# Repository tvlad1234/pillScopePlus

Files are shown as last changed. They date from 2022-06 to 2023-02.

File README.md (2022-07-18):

# pillScope Plus
Oscilloscope based around the STM32F401 Black Pill and a color LCD screen, meant to be used as an educational tool
The pillScope in its case

## Why does it exist?
The goal of this project was to create a simple and easy to build but still very usable oscillsocope. I wanted to learn the basics of how a **digital storage oscilloscope** functions, while also ending up with something which can be used as an educational tool in the lab. A short description of how oscillscopes (and this one in particular) work can be found [here](HowItWorks.md).

## Features
* -3.3V to 3.3V input range (can be increased if using attenuator probes)
* 1MOhm input impedance
* 10uS/div minimum timebase
* 1.6 MSa/S sampling rate
* On screen measurements:
  * min/max voltage
  * peak-to-peak voltage
  * frequency
* Captured waveforms can be sent to a computer over UART and analyzed in the Tektronix TekScope app
## Required parts
### Base parts:
* STM32F401CC Black Pill development board
* 128x160 ST7735-based TFT display
* 3 pushbuttons
* LM358 dual op-amp (rail-to-rail opamps should work better in this context, but this is what I had on hand)
* 2x 68kOhm resistors (to create a 1.65V offset voltage)
* 2x 500kOhm resistors (to create the input attenuator)

### Useful, but not mandatory:
* a 5V power supply
* an opto-isolated USB UART adapter
* a BNC connector, for using proper oscilloscope probes

## Schematics
The LCD screen is connected to SPI1 (PB3-SCK, PB5-MOSI, PB12-CS, PB13-RST, PB14-DC). The buttons are connected as follows:
* PB9: Up
* PB8: Select
* PB7: Down

The output of the analog frontend is connected to ADC1_IN0, which corresponds to PA0.\
The schematic of the frontend can be found in the [frontend.pdf](frontend.pdf) file.

## Using the oscilloscope
### The UI
The Select button cycles through the different parameters, which can be adjusted using the Up and Down buttons. 

### Auto calibration
Pressing Up and Down at the same time triggers the auto-calibration function. The tip and ground clip of the probed should be coupled together while calibrating. 

### Measuring things
The frontend of the instrument makes use of a virtual ground point which is 1.65V above the real ground. Because of this, the oscilloscope and the device under test must not be sharing the same ground reference. If you need to send data to the computer while measuring a device which shares ground with the scope, you should connect the computer via an opto-isolated adapter, while powering the oscilloscope from an external source.

### Saving captured wavevorms
The captured waveforms can be sent to a computer over UART.

#### CSV Output
Sending `s` (lowercase s) to the UART tells the instrument to output the captured waveform in CSV format, which is compatible with the Tektronix TekScope app.

putty

#### Direct TekScope output 
Sending `S` (capital S) tells the scope to output raw data, which can be read by a [companion app](https://github.com/tvlad1234/tekscopeIngest). This app automatically streams the captured data to TekScope, which allows almost real-time waveform analysis on the computer.
companion

## Code
The code can be compiled with `make`. The actual oscilloscope code of this project is located in `Core\Src`, the [scope.c](Core/Src/scope.c), [ui.c](Core/Src/ui.c) and [wave.c](Core/Src/wave.c) files. Feel free to take a look, as they're commented for ease of understanding.

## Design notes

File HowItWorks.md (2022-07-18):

# How does it work?
## But first of all, what's an oscilloscope?
An oscilloscope, colloquially called _scope_ is a measurement instrument which graphically displays electrical voltage in relation to time. This allows the user to visualise and analyze high-speed electrical signals which cannot be seen otherwise.

In the past, oscilloscopes were constructed using cathode ray tubes, similar to the ones found in old TVs. They worked by sweeping an electron beam across a phosphor-coated screen, which was being vertically deflected by the input signal. This would cause the screen to glow in every point struck by the beam, allowing visualisation of the input signal as a waveform. This process was purely analog and happened in real-time. As such, all measurements had to be done manually, by physically measuring the waveform on the screen. This also meant that the waveforms couldn't be stored anywhere (analog storage oscilloscopes existed but they were very uncommon). 

Most oscilloscopes nowadays are *digital storage oscillscopes*. As their name suggests, they sample and store the incoming signal in a digital manner. This way, the signal can be analyzed using a computer, making advanced and automatic measurements possible.

## How does a digital storage oscilloscope work?
### Conditioning the signal
Before it can be measured by the various components of an oscilloscope, the input signal must be conditioned in some way. This usually involves scaling and attenuating it by a component called the *analog frontend*. The actual measuring element of our instrument can only sample voltages in the 0 - 3.3V range. In order to extend this range into a useful domain, we attenuate the input signal by half and center it at around 1.65V. This is done by using a voltage divider and an op-amp to create a reference voltage and another divider and opamp to attenuate and buffer the signal. Doing so allows the instrument measure voltages ranging from -3.3V to +3.3V. The schematic of the frontend can be found in the [frontend.pdf](frontend.pdf) file.

### Converting voltage into numbers
Electrical voltage is a physical quantity which must be sampled and quantized into a numerical value. This is done by an _ADC_ (**A**nalog to **D**igital **C**onverter). The ADC used in this project is integrated into the microcontroller and it's a *successive aproximation register ADC*. This means that the ADC takes the input voltage and compares it to different voltages until it finds the closest match. Two of the main characteristics of an ADC are its resolution and maximum sampling rate. The resolution tells us how many bits it uses to represent numbers. Our ADC is 12-bit, meaning that there are 2<sup>12</sup> different values it can output. The maximum sampling rate measures how fast the ADC can measure the incoming signal. Our ADC is capable of up to 1.6 MSa/S (megasamples per second, or milions of samples per second).

### Sampling a signal
In order to digitally reconstruct a waveform, the signal must be sampled at precise intervals of time. We're achieving this by using one of the timers of our microcontroller in order to generate the timebase of our scope. This way, the ADC captures a sample on every firing of the timer. Oscilloscopes generally use dedicated hardware to trigger the sampling on precise segments of the input signal. For the sake of simplicity, our oscilloscope simulates this in software by aligning the displayed waveform with the selected trigger condition.

### Getting the data into the memory
Digital oscilloscopes usually have dedicated sample memory and hardware which handles the transfer of data from the ADC without the main processor being involved. We're using a similar approach here too, by making use of the *DMA* (**D**irect **M**emory **A**ccess) engine of the microcontroller. The processor tells the DMA to start pulling data from the ADC into a buffer in memory and then waits. Each time the ADC is triggered, a DMA transfer occurs. Once the buffer is full, the DMA stops and tells the processor that it has finished transfering data. With the sampled signal in memory, we can now display the waveform on the screen and perform different measurements.

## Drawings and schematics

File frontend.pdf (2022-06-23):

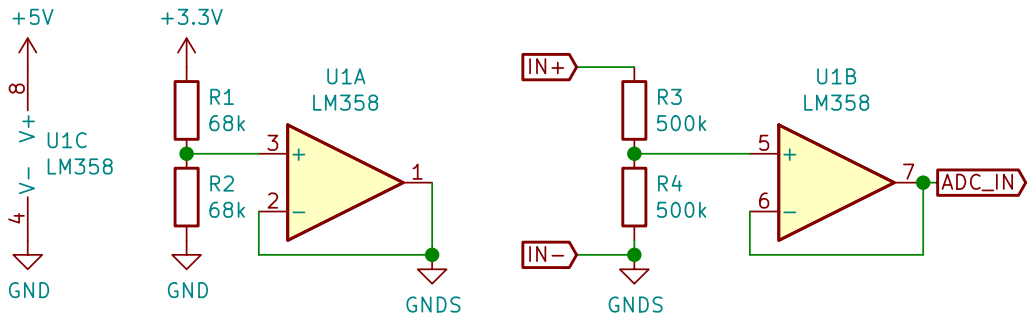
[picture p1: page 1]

File: pillScope.sch Sheet: / tvlad1234 V- 4 V+

Id: 1/1 Title: pillScope analog frontend

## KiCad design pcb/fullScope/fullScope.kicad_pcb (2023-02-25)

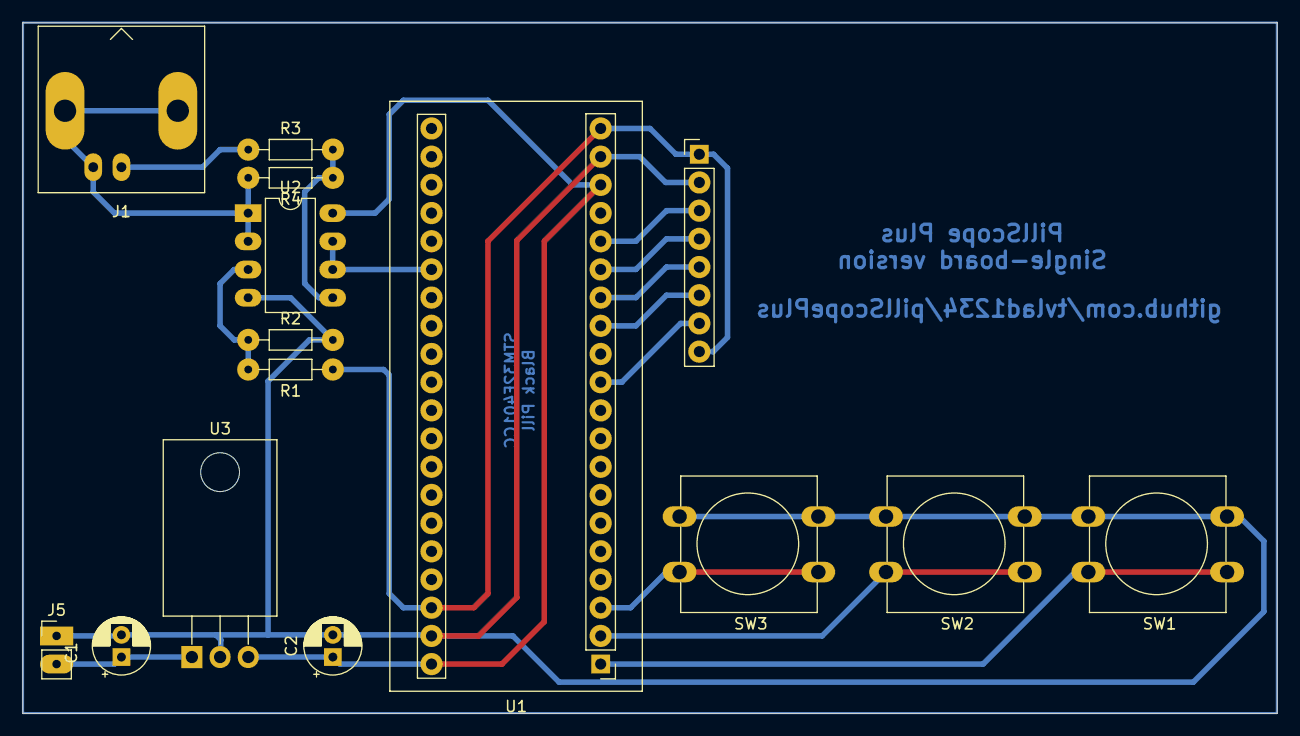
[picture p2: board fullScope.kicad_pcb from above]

Board: 2 copper layers, 113.0 x 62.2 mm, 15 parts (0 on the bottom side), 17 nets.

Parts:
C1: 10 uF; CP_Radial_D5.0mm_P2.00mm
C2: 100 uF; CP_Radial_D5.0mm_P2.00mm
J1: IN; BNC_Amphenol_B6252HB-NPP3G-50_Horizontal
J3: LCD; PinHeader_1x08_P2.54mm_Vertical
J5: Vin; PinHeader_1x02_P2.54mm_Vertical
R1, R2: R; R_Axial_DIN0204_L3.6mm_D1.6mm_P7.62mm_Horizontal
R3, R4: 500k; R_Axial_DIN0204_L3.6mm_D1.6mm_P7.62mm_Horizontal
SW1: Btn 1; SW_PUSH-12mm
SW2: Btn 2; SW_PUSH-12mm
SW3: Btn 3; SW_PUSH-12mm
U1: F401CC; YAAJ_WeAct_BlackPill_2
U2: LM358; DIP-8_W7.62mm_LongPads
U3: LM7805; TO-220-3_Horizontal_TabDown

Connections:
+3.3V: J3.1, J3.8, R1.1, U1.20 (3V3), U1.38 (3V3)
+5V: C2.1, U1.18 (5V), U1.40 (5V), U2.8 (V+), U3.3 (VO)
+9V: C1.1, J5.2, U3.1 (VI)
BTN1: SW1.1, U1.1 (PB12)
BTN2: SW2.1, U1.2 (PB13)
BTN3: SW3.1, U1.3 (PB14)
CS: J3.3, U1.16 (PB8)
DC: J3.5, U1.14 (PB6)
FE_OUT: U1.26 (PA0), U2.6 (-), U2.7
GND: C1.2, C2.2, J3.2, J5.1, R2.2, SW1.2, SW2.2, SW3.2, U1.19 (GND), U1.39 (GND), U2.4 (V-), U3.2 (GND)
GNDS: J1.2 (Ext), R4.2, U2.1, U2.2 (-)
IN+: J1.1 (In), R3.1
MOSI: J3.6, U1.13 (PB5)
unnamed: R1.2, R2.1, U2.3 (+)
unnamed: R3.2, R4.1, U2.5 (+)
RES: J3.4, U1.15 (PB7)
SCK: J3.7, U1.11 (PB3)

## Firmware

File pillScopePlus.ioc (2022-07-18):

#MicroXplorer Configuration settings - do not modify
ADC1.ExternalTrigConv=ADC_EXTERNALTRIGCONV_T3_TRGO
ADC1.IPParameters=master,NbrOfConversionFlag,ExternalTrigConv
ADC1.NbrOfConversionFlag=1
ADC1.master=1
Dma.ADC1.0.Direction=DMA_PERIPH_TO_MEMORY
Dma.ADC1.0.FIFOMode=DMA_FIFOMODE_ENABLE
Dma.ADC1.0.FIFOThreshold=DMA_FIFO_THRESHOLD_FULL
Dma.ADC1.0.Instance=DMA2_Stream0
Dma.ADC1.0.MemBurst=DMA_MBURST_SINGLE
Dma.ADC1.0.MemDataAlignment=DMA_MDATAALIGN_HALFWORD
Dma.ADC1.0.MemInc=DMA_MINC_ENABLE
Dma.ADC1.0.Mode=DMA_NORMAL
Dma.ADC1.0.PeriphBurst=DMA_PBURST_SINGLE
Dma.ADC1.0.PeriphDataAlignment=DMA_PDATAALIGN_HALFWORD
Dma.ADC1.0.PeriphInc=DMA_PINC_DISABLE
Dma.ADC1.0.Priority=DMA_PRIORITY_HIGH
Dma.ADC1.0.RequestParameters=Instance,Direction,PeriphInc,MemInc,PeriphDataAlignment,MemDataAlignment,Mode,Priority,FIFOMode,FIFOThreshold,MemBurst,PeriphBurst
Dma.MEMTOMEM.1.Direction=DMA_MEMORY_TO_MEMORY
Dma.MEMTOMEM.1.FIFOMode=DMA_FIFOMODE_ENABLE
Dma.MEMTOMEM.1.FIFOThreshold=DMA_FIFO_THRESHOLD_FULL
Dma.MEMTOMEM.1.Instance=DMA2_Stream1
Dma.MEMTOMEM.1.MemBurst=DMA_MBURST_SINGLE
Dma.MEMTOMEM.1.MemDataAlignment=DMA_MDATAALIGN_BYTE
Dma.MEMTOMEM.1.MemInc=DMA_MINC_ENABLE
Dma.MEMTOMEM.1.Mode=DMA_NORMAL
Dma.MEMTOMEM.1.PeriphBurst=DMA_PBURST_SINGLE
Dma.MEMTOMEM.1.PeriphDataAlignment=DMA_PDATAALIGN_BYTE
Dma.MEMTOMEM.1.PeriphInc=DMA_PINC_ENABLE
Dma.MEMTOMEM.1.Priority=DMA_PRIORITY_LOW
Dma.MEMTOMEM.1.RequestParameters=Instance,Direction,PeriphInc,MemInc,PeriphDataAlignment,MemDataAlignment,Mode,Priority,FIFOMode,FIFOThreshold,MemBurst,PeriphBurst
Dma.Request0=ADC1
Dma.Request1=MEMTOMEM
Dma.RequestsNb=2
File.Version=6
GPIO.groupedBy=Group By Peripherals
KeepUserPlacement=false
Mcu.CPN=STM32F401CCU6
Mcu.Family=STM32F4
Mcu.IP0=ADC1
Mcu.IP1=DMA
Mcu.IP2=NVIC
Mcu.IP3=RCC
Mcu.IP4=SPI1
Mcu.IP5=SYS
Mcu.IP6=TIM3
Mcu.IP7=USART1
Mcu.IPNb=8
Mcu.Name=STM32F401C(B-C)Ux
Mcu.Package=UFQFPN48
Mcu.Pin0=PC13-ANTI_TAMP
Mcu.Pin1=PH0 - OSC_IN
Mcu.Pin10=PA14
Mcu.Pin11=PB3
Mcu.Pin12=PB5
Mcu.Pin13=PB7
Mcu.Pin14=PB8
Mcu.Pin15=PB9
Mcu.Pin16=VP_SYS_VS_Systick
Mcu.Pin17=VP_TIM3_VS_ClockSourceINT
Mcu.Pin2=PH1 - OSC_OUT
Mcu.Pin3=PA0-WKUP
Mcu.Pin4=PB12
Mcu.Pin5=PB13
Mcu.Pin6=PB14
Mcu.Pin7=PA9
Mcu.Pin8=PA10
Mcu.Pin9=PA13
Mcu.PinsNb=18
Mcu.ThirdPartyNb=0
Mcu.UserConstants=
Mcu.UserName=STM32F401CCUx
MxCube.Version=6.5.0
MxDb.Version=DB.6.0.50
NVIC.BusFault_IRQn=true\:0\:0\:false\:false\:true\:false\:false\:true
NVIC.DMA2_Stream0_IRQn=true\:0\:0\:false\:false\:true\:false\:true\:true
NVIC.DMA2_Stream1_IRQn=true\:0\:0\:false\:false\:true\:true\:true\:true
NVIC.DebugMonitor_IRQn=true\:0\:0\:false\:false\:true\:false\:false\:true
NVIC.ForceEnableDMAVector=true
NVIC.HardFault_IRQn=true\:0\:0\:false\:false\:true\:false\:false\:true
NVIC.MemoryManagement_IRQn=true\:0\:0\:false\:false\:true\:false\:false\:true
NVIC.NonMaskableInt_IRQn=true\:0\:0\:false\:false\:true\:false\:false\:true
NVIC.PendSV_IRQn=true\:0\:0\:false\:false\:true\:false\:false\:true
NVIC.PriorityGroup=NVIC_PRIORITYGROUP_4
NVIC.SVCall_IRQn=true\:0\:0\:false\:false\:true\:false\:false\:true
NVIC.SysTick_IRQn=true\:15\:0\:false\:false\:true\:false\:true\:true
NVIC.USART1_IRQn=true\:0\:0\:false\:false\:true\:true\:true\:true
NVIC.UsageFault_IRQn=true\:0\:0\:false\:false\:true\:false\:false\:true
PA0-WKUP.Signal=ADCx_IN0
PA10.Mode=Asynchronous
PA10.Signal=USART1_RX
PA13.Mode=Serial_Wire
PA13.Signal=SYS_JTMS-SWDIO
PA14.Mode=Serial_Wire
PA14.Signal=SYS_JTCK-SWCLK
PA9.Mode=Asynchronous
PA9.Signal=USART1_TX
PB12.GPIOParameters=GPIO_Label
PB12.GPIO_Label=ST7735_CS
PB12.Locked=true
PB12.Signal=GPIO_Output
PB13.GPIOParameters=GPIO_Label
PB13.GPIO_Label=ST7735_RES
PB13.Locked=true
PB13.Signal=GPIO_Output
PB14.GPIOParameters=GPIO_Label
PB14.GPIO_Label=ST7735_DC
PB14.Locked=true
PB14.Signal=GPIO_Output
PB3.Locked=true
PB3.Mode=TX_Only_Simplex_Unidirect_Master
PB3.Signal=SPI1_SCK
PB5.Locked=true
PB5.Mode=TX_Only_Simplex_Unidirect_Master
PB5.Signal=SPI1_MOSI
PB7.GPIOParameters=GPIO_PuPd,GPIO_Label
PB7.GPIO_Label=BTN1
PB7.GPIO_PuPd=GPIO_PULLUP
PB7.Locked=true
PB7.Signal=GPIO_Input
PB8.GPIOParameters=GPIO_PuPd,GPIO_Label
PB8.GPIO_Label=BTN2
PB8.GPIO_PuPd=GPIO_PULLUP
PB8.Locked=true
PB8.Signal=GPIO_Input
PB9.GPIOParameters=GPIO_PuPd,GPIO_Label
PB9.GPIO_Label=BTN3
PB9.GPIO_PuPd=GPIO_PULLUP
PB9.Locked=true
PB9.Signal=GPIO_Input
PC13-ANTI_TAMP.GPIOParameters=GPIO_Label
PC13-ANTI_TAMP.GPIO_Label=LED
PC13-ANTI_TAMP.Locked=true
PC13-ANTI_TAMP.Signal=GPIO_Output
PH0\ -\ OSC_IN.Mode=HSE-External-Oscillator
PH0\ -\ OSC_IN.Signal=RCC_OSC_IN
PH1\ -\ OSC_OUT.Mode=HSE-External-Oscillator
PH1\ -\ OSC_OUT.Signal=RCC_OSC_OUT
PinOutPanel.RotationAngle=0
ProjectManager.AskForMigrate=true
ProjectManager.BackupPrevious=false
ProjectManager.CompilerOptimize=6
ProjectManager.ComputerToolchain=false
ProjectManager.CoupleFile=false
ProjectManager.CustomerFirmwarePackage=
ProjectManager.DefaultFWLocation=true
ProjectManager.DeletePrevious=true
ProjectManager.DeviceId=STM32F401CCUx
ProjectManager.FirmwarePackage=STM32Cube FW_F4 V1.27.0
ProjectManager.FreePins=false
ProjectManager.HalAssertFull=false
ProjectManager.HeapSize=0x200
ProjectManager.KeepUserCode=true
ProjectManager.LastFirmware=false
ProjectManager.LibraryCopy=0
ProjectManager.MainLocation=Core/Src
ProjectManager.NoMain=false
ProjectManager.PreviousToolchain=
ProjectManager.ProjectBuild=false
ProjectManager.ProjectFileName=pillScopePlus.ioc
ProjectManager.ProjectName=pillScopePlus
ProjectManager.RegisterCallBack=
ProjectManager.StackSize=0x400
ProjectManager.TargetToolchain=Makefile
ProjectManager.ToolChainLocation=
ProjectManager.UnderRoot=false
ProjectManager.functionlistsort=1-SystemClock_Config-RCC-false-HAL-false,2-MX_GPIO_Init-GPIO-false-HAL-true,3-MX_DMA_Init-DMA-false-HAL-true,4-MX_ADC1_Init-ADC1-false-HAL-true,5-MX_SPI1_Init-SPI1-false-HAL-true,6-MX_TIM3_Init-TIM3-false-HAL-true,7-MX_USB_DEVICE_Init-USB_DEVICE-false-HAL-false,7-MX_USART1_UART_Init-USART1-false-HAL-true
RCC.48MHZClocksFreq_Value=50000000
RCC.AHBFreq_Value=100000000
RCC.APB1CLKDivider=RCC_HCLK_DIV2
RCC.APB1Freq_Value=50000000
RCC.APB1TimFreq_Value=100000000
RCC.APB2Freq_Value=100000000
RCC.APB2TimFreq_Value=100000000
RCC.CortexFreq_Value=100000000
RCC.FCLKCortexFreq_Value=100000000
RCC.HCLKFreq_Value=100000000
RCC.HSE_VALUE=25000000
RCC.HSI_VALUE=16000000
RCC.I2SClocksFreq_Value=96000000
RCC.IPParameters=48MHZClocksFreq_Value,AHBFreq_Value,APB1CLKDivider,APB1Freq_Value,APB1TimFreq_Value,APB2Freq_Value,APB2TimFreq_Value,CortexFreq_Value,FCLKCortexFreq_Value,HCLKFreq_Value,HSE_VALUE,HSI_VALUE,I2SClocksFreq_Value,LSE_VALUE,LSI_VALUE,PLLCLKFreq_Value,PLLM,PLLN,PLLQCLKFreq_Value,PLLSourceVirtual,RTCFreq_Value,RTCHSEDivFreq_Value,SYSCLKFreq_VALUE,SYSCLKSource,VCOI2SOutputFreq_Value,VCOInputFreq_Value,VCOOutputFreq_Value,VcooutputI2S
RCC.LSE_VALUE=32768
RCC.LSI_VALUE=32000
RCC.PLLCLKFreq_Value=100000000
RCC.PLLM=25
RCC.PLLN=200
RCC.PLLQCLKFreq_Value=50000000
RCC.PLLSourceVirtual=RCC_PLLSOURCE_HSE
RCC.RTCFreq_Value=32000
RCC.RTCHSEDivFreq_Value=12500000
RCC.SYSCLKFreq_VALUE=100000000
RCC.SYSCLKSource=RCC_SYSCLKSOURCE_PLLCLK
RCC.VCOI2SOutputFreq_Value=192000000
RCC.VCOInputFreq_Value=1000000
RCC.VCOOutputFreq_Value=200000000
RCC.VcooutputI2S=96000000
SH.ADCx_IN0.0=ADC1_IN0,IN0
SH.ADCx_IN0.ConfNb=1
SPI1.BaudRatePrescaler=SPI_BAUDRATEPRESCALER_4
SPI1.CalculateBaudRate=25.0 MBits/s
SPI1.Direction=SPI_DIRECTION_2LINES
SPI1.IPParameters=VirtualType,Mode,Direction,CalculateBaudRate,BaudRatePrescaler
SPI1.Mode=SPI_MODE_MASTER
SPI1.VirtualType=VM_MASTER
TIM3.IPParameters=TIM_MasterOutputTrigger
TIM3.TIM_MasterOutputTrigger=TIM_TRGO_UPDATE
USART1.BaudRate=9600
USART1.IPParameters=VirtualMode,BaudRate
USART1.VirtualMode=VM_ASYNC
VP_SYS_VS_Systick.Mode=SysTick
VP_SYS_VS_Systick.Signal=SYS_VS_Systick
VP_TIM3_VS_ClockSourceINT.Mode=Internal
VP_TIM3_VS_ClockSourceINT.Signal=TIM3_VS_ClockSourceINT
board=custom

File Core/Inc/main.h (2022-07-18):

/* USER CODE BEGIN Header */
/**
 ******************************************************************************
 * @file           : main.h
 * @brief          : Header for main.c file.
 *                   This file contains the common defines of the application.
 ******************************************************************************
 * @attention
 *
 * Copyright (c) 2022 STMicroelectronics.
 * All rights reserved.
 *
 * This software is licensed under terms that can be found in the LICENSE file
 * in the root directory of this software component.
 * If no LICENSE file comes with this software, it is provided AS-IS.
 *
 ******************************************************************************
 */
/* USER CODE END Header */

/* Define to prevent recursive inclusion -------------------------------------*/
#ifndef __MAIN_H
#define __MAIN_H

#ifdef __cplusplus
extern "C" {
#endif

/* Includes ------------------------------------------------------------------*/
#include "stm32f4xx_hal.h"

/* Private includes ----------------------------------------------------------*/
/* USER CODE BEGIN Includes */
#include "st7735.h"
#include "gfx.h"
/* USER CODE END Includes */

/* Exported types ------------------------------------------------------------*/
/* USER CODE BEGIN ET */

/* USER CODE END ET */

/* Exported constants --------------------------------------------------------*/
/* USER CODE BEGIN EC */

/* USER CODE END EC */

/* Exported macro ------------------------------------------------------------*/
/* USER CODE BEGIN EM */

/* USER CODE END EM */

/* Exported functions prototypes ---------------------------------------------*/
void Error_Handler(void);

/* USER CODE BEGIN EFP */
  void printFloat(float v, int decimalDigits, char s[]);
  void *dma_memcpy(void *destination, const void *source, size_t num);
/* USER CODE END EFP */

/* Private defines -----------------------------------------------------------*/
#define LED_Pin GPIO_PIN_13
#define LED_GPIO_Port GPIOC
#define ST7735_CS_Pin GPIO_PIN_12
#define ST7735_CS_GPIO_Port GPIOB
#define ST7735_RES_Pin GPIO_PIN_13
#define ST7735_RES_GPIO_Port GPIOB
#define ST7735_DC_Pin GPIO_PIN_14
#define ST7735_DC_GPIO_Port GPIOB
#define BTN1_Pin GPIO_PIN_7
#define BTN1_GPIO_Port GPIOB
#define BTN2_Pin GPIO_PIN_8
#define BTN2_GPIO_Port GPIOB
#define BTN3_Pin GPIO_PIN_9
#define BTN3_GPIO_Port GPIOB
/* USER CODE BEGIN Private defines */

/* USER CODE END Private defines */

#ifdef __cplusplus
}
#endif

#endif /* __MAIN_H */

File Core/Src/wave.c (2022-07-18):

#include "main.h"
#include "scope.h"
#include "wave.h"

#define WHITE ST7735_WHITE
#define BLACK ST7735_BLACK
#define WAVE_COLOR ST7735_YELLOW

// All kinds of variables, you'll see what these do in scope.c
extern uint16_t adcBuf[BUFFER_LEN];
extern int atten;
extern float vdiv;
extern float trigVoltage;
extern uint8_t trig, trigged;
extern int trigPoint;

extern float tdiv;
extern uint32_t sampRate;
extern float sampPer;

extern float maxVoltage, minVoltage;
extern float measuredFreq, sigPer;

extern float offsetVoltage;

uint8_t topClip, bottomClip; // Whether or not we're clipping through the graticule

// Convert ADC sample to voltage at frontend input
float frontendVoltage(uint16_t samp)
{
    return 2 * (((3.3 * samp) / 4096.0) - offsetVoltage);
}

// Convert ADC sample to voltage at ADC input
float adcToVoltage(uint16_t samp)
{
    return (3.3 * samp) / 4096.0;
}

// This function draws the graticule onto the screen
void drawGraticule(uint16_t divx, uint16_t divy, uint16_t pix)
{
    uint16_t wit = divx * pix;
    uint16_t hei = divy * pix;

    for (int i = 0; i <= wit; i += pix)
        dottedVLine(i, 0, hei);

    for (int i = 0; i <= hei; i += pix)
        dottedHLine(0, i, wit);
}

// This function draws a dotted horizontal line, used for drawing the graticule
void dottedHLine(int x, int y, int l)
{
    for (int i = 0; i <= l; i++)
    {
        if (i % 2)
            drawPixel(x + i, y, WHITE);
        else
            drawPixel(x + i, y, BLACK);
    }
}

// This function draws a dotted vertical line, used for drawing the graticule
void dottedVLine(int x, int y, int l)
{
    for (int i = 0; i <= l; i++)
    {
        if (i % 2)
            drawPixel(x, y + i, WHITE);
        else
            drawPixel(x, y + i, BLACK);
    }
}

// Draw the waveform trace on the screen
void drawTrace(uint16_t buf[], uint16_t trigPoint, uint16_t col)
{

    maxVoltage = LOWER_VOLTAGE;
    minVoltage = UPPER_VOLTAGE;

    for (int i = 0; i <= BUFFER_LEN / 2; i++)
    {
        // If we're looping through the buffer, let's compute the minimum and maximum voltage values while we're at it
        float voltage1 = atten * frontendVoltage(buf[i + trigPoint]);
        float voltage2 = atten * frontendVoltage(buf[i + trigPoint + 1]);
        if (voltage2 > maxVoltage)
            maxVoltage = voltage2;
        if (voltage2 < minVoltage)
            minVoltage = voltage2;

        // Draw lines between sample points
        topClip = 0;
        bottomClip = 0;
        int16_t y1 = (PIXDIV * YDIV / 2 - 1) - (voltage1 * PIXDIV / vdiv);
        int16_t y2 = (PIXDIV * YDIV / 2 - 1) - (voltage2 * PIXDIV / vdiv);
        if (y1 > YDIV * PIXDIV)
        {
            y1 = YDIV * PIXDIV;
            bottomClip = 1;
        }
        if (y2 > YDIV * PIXDIV)
        {
            y2 = YDIV * PIXDIV;
            bottomClip = 1;
        }
        if (y1 < 0)
        {
            y1 = 0;
            topClip = 1;
        }
        if (y2 < 0)
        {
            y2 = 0;
            topClip = 1;
        }
        drawLine(i, y1, i + 1, y2, col);
    }
}

// Draw the trace and graticule on the screen
void traceScreen()
{
    drawGraticule(XDIV, YDIV, PIXDIV); // Draw the graticule
    drawTrace(adcBuf, trigPoint, WAVE_COLOR);
}
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

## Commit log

2022-07-13 boot logo, removed USB, increased sample rate
2023-02-25 Add PCB files
    [fullScope.kicad_pcb, fullScope.kicad_sch]
